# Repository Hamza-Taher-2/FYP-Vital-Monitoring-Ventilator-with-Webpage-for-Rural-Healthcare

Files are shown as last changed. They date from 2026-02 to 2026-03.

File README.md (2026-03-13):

# FYP-Vital-Monitoring-Ventilator-with-Webpage-for-Rural-Healthcare

Smart Portable Vital Monitoring Ventilator

Student: Muhammad Hamza Taher
Supervisor: Dr Munira Raja
Assessor: Dr Roberto Ferrero

A low-cost portable ventilator and vital monitoring system designed for rural healthcare environments with limited access to electricity and medical infrastructure.

The system integrates patient monitoring sensors, a Raspberry Pi Pico W microcontroller, wireless data transmission, and a solar-powered energy system to create a portable and sustainable medical support device.

Project Overview

- Rural areas in South Asia suffer from high levels of chronic respiratory diseases, contributing to approximately 12% of deaths across the region. 

- Poster Update 5

- Combined with limited access to medical facilities, this leads to increased mortality rates.

- This project aims to develop a cost-effective monitoring ventilator system that can assist healthcare workers by:

- Monitoring patient vital signs

- Providing ventilation assistance

- Transmitting medical data through a webpage

- Operating in low-power environments using solar energy

Key Features

- Portable ventilator monitoring system

- Real-time vital sign monitoring

- Wireless data transmission via WiFi

- Fast responsive companion webpage

- Alarm system for abnormal readings

- Solar powered charging system

- Adjustable ventilator operation

- Low-cost hardware design

System Architecture

- The system is built around a Raspberry Pi Pico W, which manages:

- Sensor data acquisition

- Motor control for ventilation

- LCD display updates

- Wireless webpage communication

- The microcontroller balances these tasks to avoid signal starvation and maintain stable operation. 

Hardware Components
- Component	Purpose
- Raspberry Pi Pico W	Main microcontroller
- Vital Sign Sensors	Monitor patient health data
- Servo / Motor System	Controls ventilator airflow
- LCD Display	Displays patient data locally
- LiPo Battery	Portable power source
- Solar Tracker	Tracks sunlight to maximise energy capture
- Solar Panel	Renewable power supply
- ON/OFF Switch	Power control
- Solar Power System

- The system includes a solar tracking module to support operation in areas with limited electricity.

The solar tracker:

- Tracks the sun throughout the day

- Maximises solar panel efficiency

- Converts solar energy into a stable 5V output

- Charges a rechargeable LiPo battery

- This allows the ventilator to operate in off-grid environments. 

Electronics Design

- The circuit was designed using KiCad.

- Key features of the schematic include:

- Shared 3.3V power rail

- I2C communication between sensors and Pico

- Dedicated power subsystem for the LiPo battery

- Direct servo connection for ventilator control

- ON/OFF power control system

- The device boots and initializes sensors before establishing WiFi communication.

Sensor Calibration

- All sensors were calibrated against known reference devices to ensure reliable monitoring.

Temperature

- Reference: Medical thermometer

- Adjustment: Code libraries

- Issues: Sensor refresh rate

Air Pressure

- Reference: Manufacturer datasheet

- Adjustment: Code libraries

- Issues: Tube leakage

Heart Rate

- Reference: Apple Watch

- Adjustment: Library calibration

- Issues: Tube pressure affecting readings

Blood Oxygen (SpO₂)

- Reference: Apple Watch

- Adjustment: Library calibration

- Issues: Adjustments required for darker skin tones

Market Context

- The global medical technology market is expected to reach:

- $712.9 billion by 2030

- IoT monitoring devices represent one of the largest growth sectors, accounting for approximately 18% of the market share. 

- This project demonstrates how low-cost embedded systems can contribute to this growing healthcare technology space.

Future Improvements

- Potential future developments include:

- Improved solar tracker battery system

- Longer wireless transmission range

- Secure global patient database

- Data encryption for medical compliance

- Additional sensors (e.g., ECG monitoring)

- Medical regulatory compliance (WHO standards)

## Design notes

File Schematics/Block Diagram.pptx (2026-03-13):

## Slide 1

Initial Design

Motor

Display - LCD

S1 -
Heart Rate and Blood Oxygen

S2 –
Temperature

MC1 –
Raspberry Pi Pico W

B3 –
Speed

MC2 –
Raspberry Pi Zero 2

Web Page

S3 –
Pressure

KEY
Sensor
Microcontroller
Buttons
Display
Webpage
Motor

B2 –
Volume

B1 –
On/Off

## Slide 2

New Design

B1 –
On/Off

S1 -
Heart Rate and Blood Oxygen

S2 –
Temperature

MC2 –
Raspberry Pi Pico W

MC3 –
Raspberry Pi Pico W

Web Page

S3 –
Pressure

Display - LCD

KEY
Sensor
Microcontroller
Buttons
Display
Webpage
Motor

B2 –
Volume

MC1 –
Raspberry Pi Pico H

Motor

B3 –
Speed

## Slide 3

Old Design

B1 –
On/Off

S1 -
Heart Rate and Blood Oxygen

S2 –
Temperature

MC1 –
Raspberry Pi Pico W

MC2 –
Raspberry Pi Zero 2

Web Page

S3 –
Pressure

Display - LCD

KEY
Sensor
Microcontroller
Buttons
Display
Webpage
Motor

B2 –
Volume

MC1 –
Raspberry Pi Pico H

Motor

B3 –
Speed

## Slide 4

Sem 2 Design

Motor

Speaker

Display - LCD

Heart Rate and Blood Oxygen

Temperature

Raspberry Pi Pico W

Web Page

KEY
Sensor
Microcontroller
Buttons
Display
Webpage
Motor
Speaker

Pressure

B2 –
Volume

B3 –
Speed

B1 –
On/Off

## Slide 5

Temperature

Pressure

Heart Rate

Blood Oxygen

Raspberry Pi Pico W

Newest Design

B1 – On/Off

Display - LCD

B3 – Speed

B2 – Volume

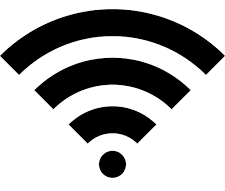
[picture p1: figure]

Speaker

Motor

Web Page

LDR

Pi Pico H

Motor

Button ON/OFF

Battery

Solar Panel

Converter

Output

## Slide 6

LDR

Pi Pico H

Motor

Button ON/OFF

Battery

Solar

Solar Panel

Converter

Output

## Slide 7

Pressure

Heart Rate

Temperature

Pi Pico W

Blood Oxygen

Solar Panel

Button ON/OFF

LDR

B1 – On/Off

Display - LCD

Converter

Pi Pico H

B3 – Speed

B2 – Volume

Speaker

Web Page

Motor

Output

Battery

Motor

NEW NEWEST Design

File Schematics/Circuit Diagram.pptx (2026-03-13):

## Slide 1

Heart D

Heart C

Heart GND

OLD

Pressure V + Temp V + Heart V

Pressure Signal

Pressure GND

Temp GND

Temp signal

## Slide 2

NEW

Heart GND

Pressure V + Temp V + Heart V + Speaker V + LCD V +

Heart D + LCD SDA

Heart C + LCD SCL

Pressure Signal

Speaker GND + Pressure GND

Temp GND

LCD GND

Speaker Signal

Temp signal

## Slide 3

MOTOR

Heart GND

Pressure V + Temp V + Heart V + Speaker V +
LCD V + P1 V + P2 V + Servo V + Humidity V

Heart D + LCD SDA

Heart C + LCD SCL

Servo GND

Pressure Signal

P1 Signal

P2 Signal

Speaker GND + Pressure GND

Temp GND

P1 GND + P2 GND + Humidity GND

LCD GND

Humidity Signal

Speaker Signal

Servo Signal

Temp signal

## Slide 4

FULL

LCD

SCL

SDA

Pressure

Heart

Pot 1

Pot 2

+3V3 Battery

Humid

Servo

Temp

Servo

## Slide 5

Solar Panel

Solar Board

Battery

Switch

SOLAR

LDR

LDR

Resistor

Resistor

Servo

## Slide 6

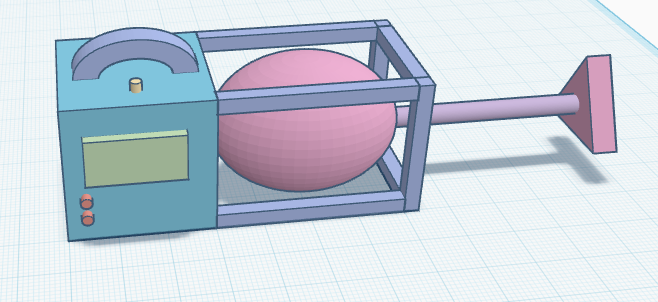
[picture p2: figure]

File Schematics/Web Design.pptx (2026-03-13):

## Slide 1

Dr Akhter’s Monitor Log

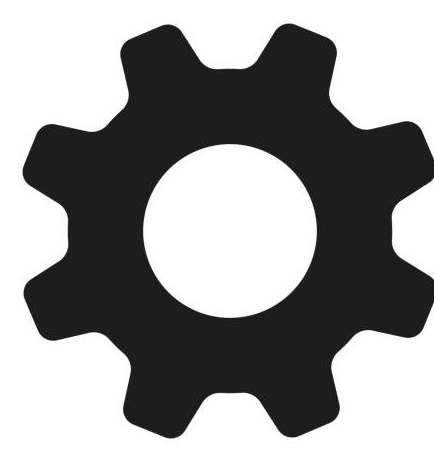
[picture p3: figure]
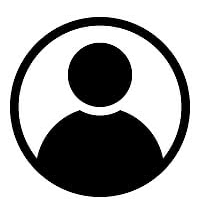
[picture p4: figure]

Patient Information
Patient Name: Simran Khan
Patient ID: 19023
Location: Khulna, Bangladesh
Time: 12:08 BST

Sensor Readings
Heart Rate: 72 BPM
Average Heart Rate: 75 BPM
Peak Heart Rate: 112 BPM
Lowest Heart Rate: 64 BPM
Temperature: 23°C
Blood Oxygen: 98% SpO2
Air Pressure: 80 PaO2
Humidity: 80% HD

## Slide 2

Dr Akhter’s Monitor Log

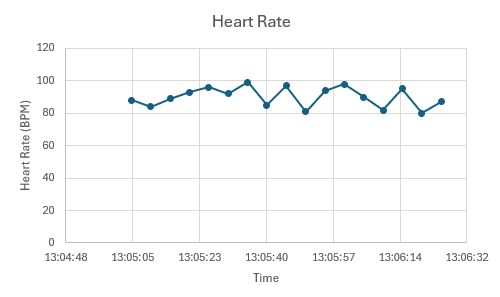
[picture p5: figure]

Patient Information
Patient Name: Simran Khan
Patient ID: 19023
Location: Khulna, Bangladesh
Date: 09/02/2026
Time: 12:08 BST

Sensor Readings
Heart Rate: 72 BPM
Average Heart Rate: 75 BPM
Peak Heart Rate: 112 BPM
Lowest Heart Rate: 64 BPM
Temperature: 23°C
Blood Oxygen: 98% SpO2
Air Pressure: 80 PaO2
Humidity: 80% HD

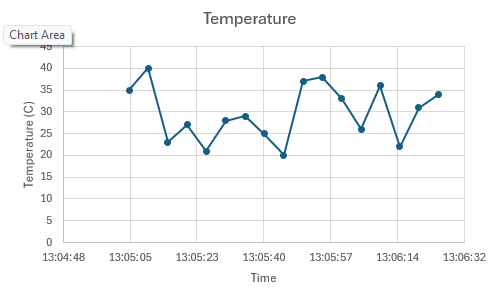
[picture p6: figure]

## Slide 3

Could add diagrams of the heart rate, etc

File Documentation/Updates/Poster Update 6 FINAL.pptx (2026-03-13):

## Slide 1

Smart Portable Vital Monitoring Ventilator with a Companion Webpage for Rural Healthcare

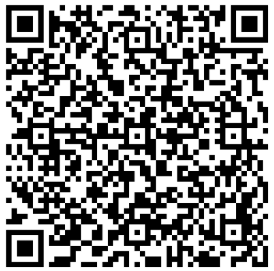
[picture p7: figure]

GitHub

Student: Muhammad Hamza Taher

ID: 201723236

Supervisor: Dr Munira Raja

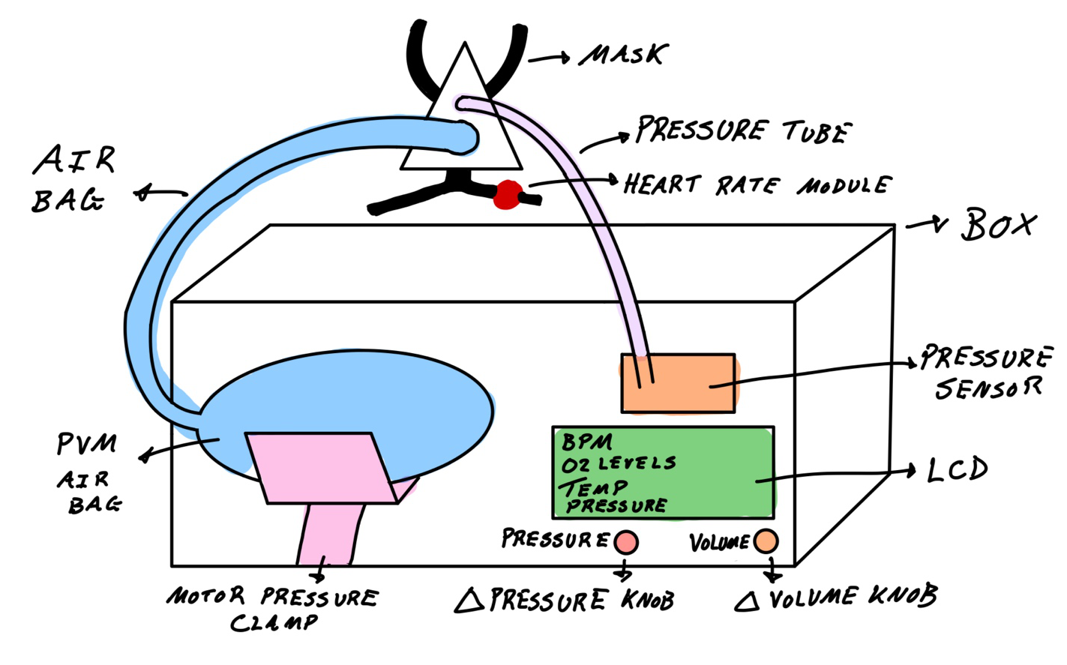
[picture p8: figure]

Fig. 1: Initial Sketch

Assessor: Dr Roberto Ferrero

The design (in Fig. 1) incorporates the following features:
- Pico W to detect patients vitals to display on an LCD and webpage for remote monitoring [2]
- Potentiometer-controlled motor acts as an adjustable ventilator [3]
- Rechargeable battery and alarm system.

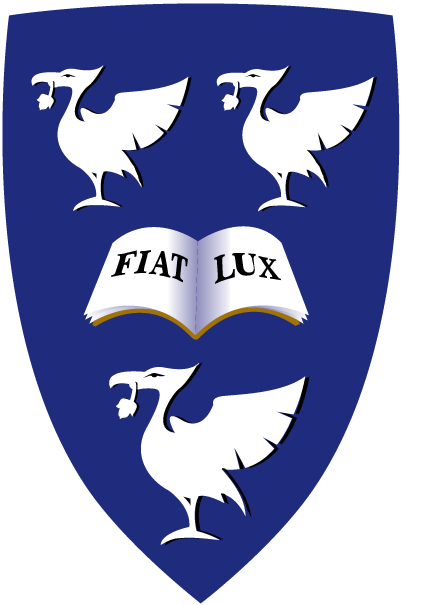
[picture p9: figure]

Introduction

This project aims to develop a system to remotely support health monitoring in rural South Asia via data transmission of vital data to nearby hospitals. [1]
Objectives include:
- Utilising calibrated sensors to measure patient’s vitals
- Display the patient’s vital data on an LCD and Webpage
- Functional ventilator with adjustable setting (speed and pressure)
- Rechargeable battery system for longer duration of use
- Working alarm system activated when thresholds are exceeded

Background Information

The system is a monitoring aid, not a replacement for professional equipment [6].
Future updates includes data encryption and compliance with medical standards (Fig.6)
Design specifications are as follows:
- Heart Rate accuracy: ± 5 BPM
- Web latency: 15ms
- Battery duration: 20 Hours
- Alarm trigger success: 90%

Fig. 6: 3D Mock Up of Design

Specification

The Pico W splits its attention between the motor, LCD, webpage, and sessors to manage signals to stop starvation for a cost-effective design [4].
For areas with low access to power, a solar tracker was designed to track the sun to convert solar energy to a stable 5V output (in Fig.4) [5].

Fig. 4: Block Diagram of Ventilator and Solar Tracker

The KiCAD schematic (in Fig.5) shows a shared 3.3V input and ground with i2C signal pins connecting to a Pico pin. The rechargeable LIPO battery uses a power sub-circuit and direct connection to the servo. Controlled by an ON/OFF button with the device booting until connected to WIFI.

Fig. 5: Ventilator System Schematic

Implementation and Design

Estimated to grow to $712.9 bn by 2030, the medical technology market is a fast-growing industry with IoT monitoring devices at the highest market share of 25%,(in Fig.2) reaching $40.7 bn by 2030 [7]

Fig. 2: Market Data of Medical Data

Rural areas in South Asia have high levels of chronic respiratory diseases resulting in 12% of deaths across all regions [8]. Paired with low medical access results in high mortality rates.

Fig. 3: Air Pollution in South Asia

Market Research

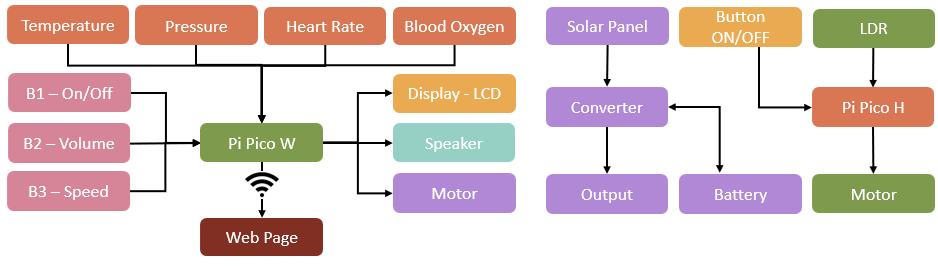
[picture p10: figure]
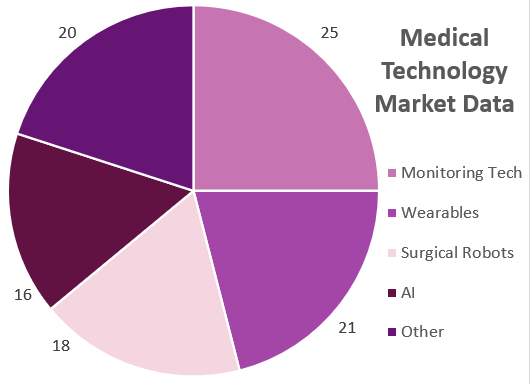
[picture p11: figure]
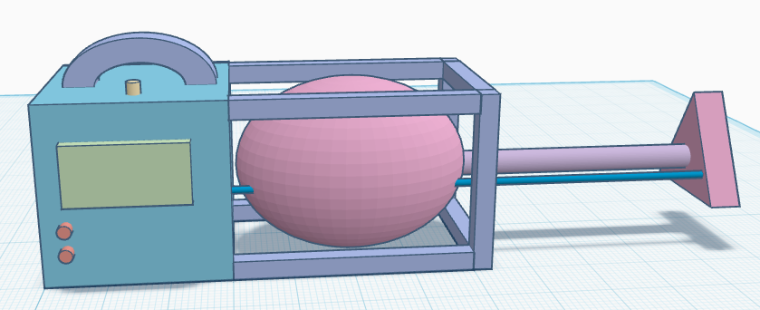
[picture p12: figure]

References

1. Webster, J. (2017). Medical Instrumentation: Application and Design.
2. Analog Devices (2019). MAX30102 Pulse Oximeter and Heart-Rate Sensor Datasheet.
3. Just Do Electronics (2022). DIY Ventilator Using Arduino.
4. Raspberry Pi Foundation (2021). Getting Started with Raspberry Pi Pico.
5. Circuit Digest (2020). Sun Tracking Solar Panel Using Arduino
6. World Health Organization (2019). Technical Specifications for Medical Devices.
7. Nagarro (2024). Medical Devices Market Summary
8. IQAir (2024). Global Air Quality Map

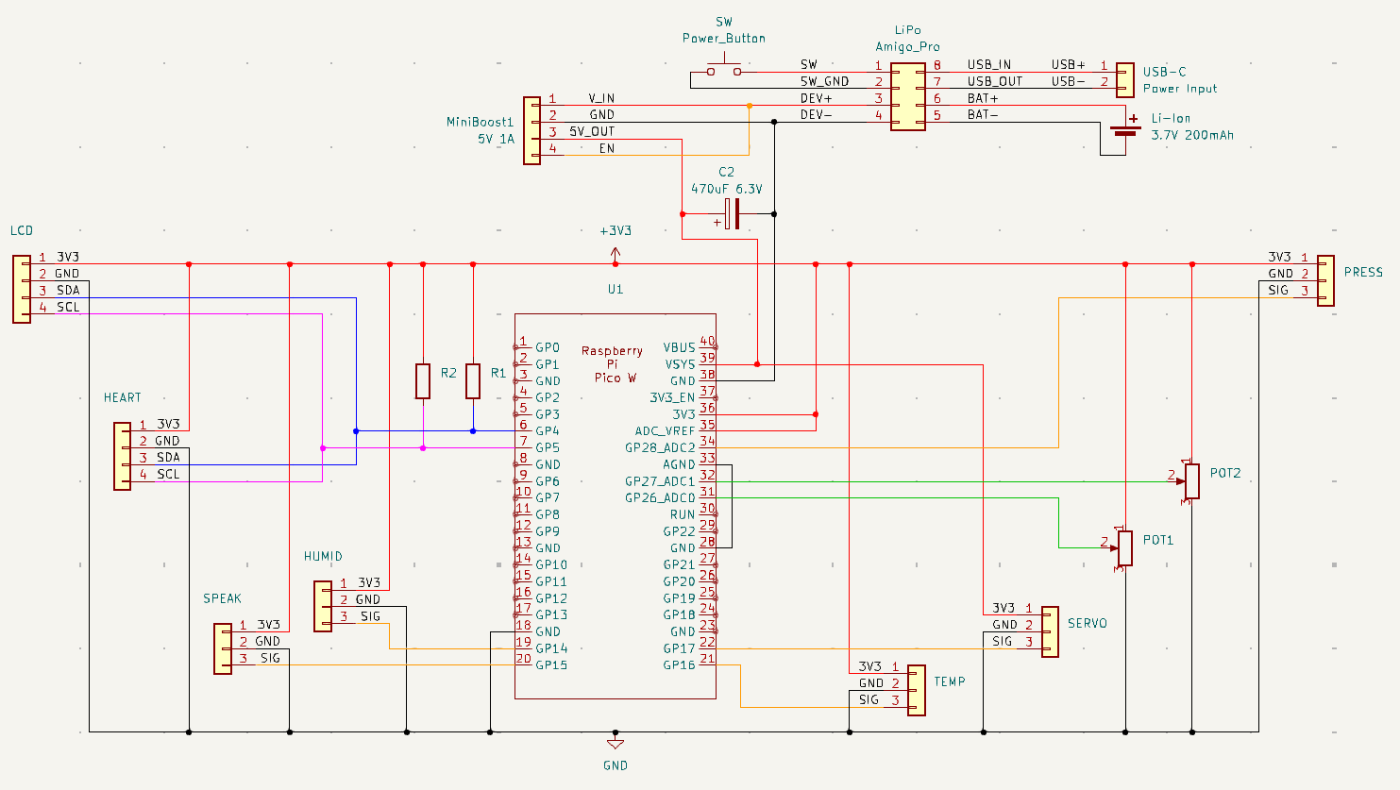
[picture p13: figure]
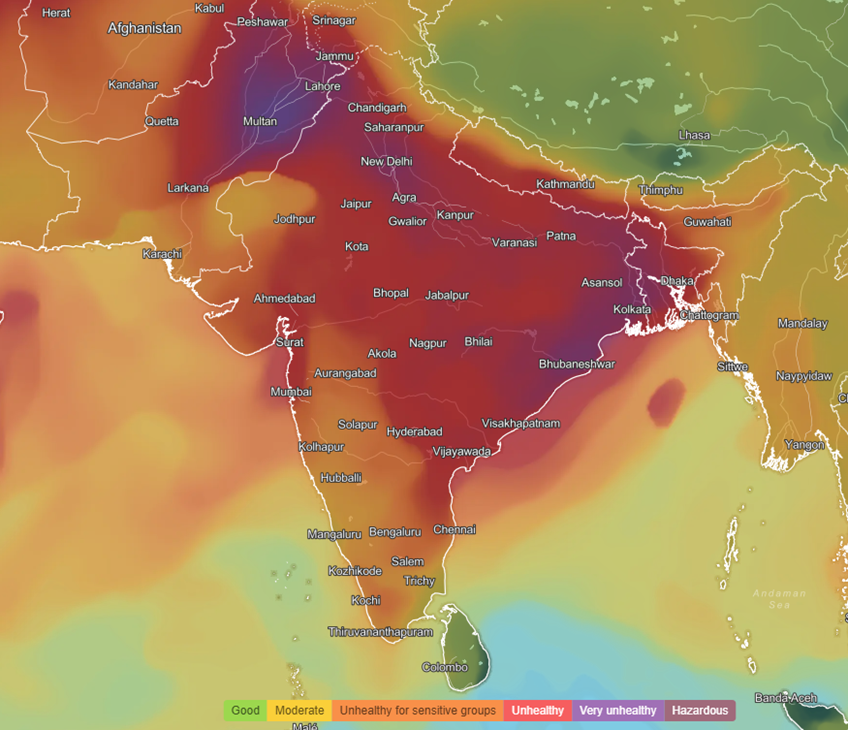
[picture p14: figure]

Sensor Calibration Results and Discussion

Conclusion

Temperature:
Figure 8 shows
Calibrated against:
- Thermometer
Adjusted using:
- Code Libraries
Issues came from:
- refresh rate adjustment

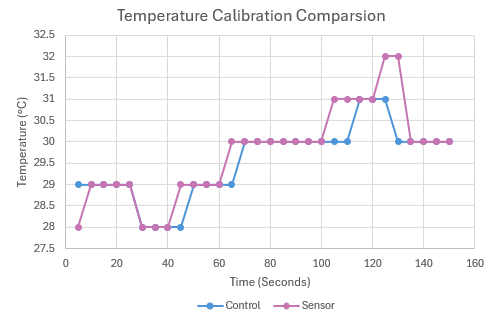
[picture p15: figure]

Fig. 8: Temperature Calibration Graph

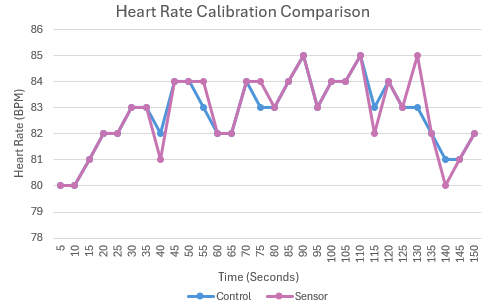
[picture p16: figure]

Fig. 7: Heart Rate Calibration Graph

Heart Rate:
Figure 7 shows
Calibrated against:
- Apple Watch
Adjusted using:
- Code Libraries
Issues came from:
- Adjustments for darker skin

The project was an overall success as the aims were met through the following objectives:
- Responsive data displays
- Calibrated sensors for vital reading
- Adjustable functional ventilator
- Alarm system active when exceeded thresholds
Further improvements include:
- Larger battery capacity for longer time of usage
- Longer transmission range for instant medical data refresh rate
- Global patient database with encryption data
- Added sensors like ECG for better scope of information

Air Pressure:
Figure 9 shows
Calibrated against:
- Medical tool
Adjusted using:
- Code Libraries
Issues came from:
- Tube leakages and diameter

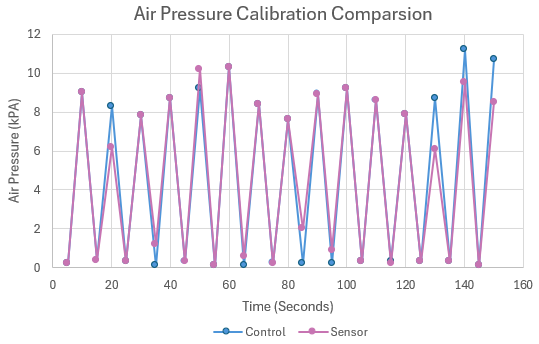
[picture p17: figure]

Fig. 9: Air Pressure Calibration Graph

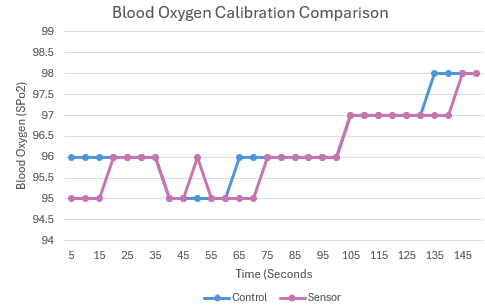
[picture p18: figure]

Fig. 10: Blood Oxygen Calibration Graph

Blood Oxygen:
Figure 10 shows
Calibrated against:
- Apple Watch
Adjusted using:
- Code Libraries
Issues came from:
- Adjustments for darker skin

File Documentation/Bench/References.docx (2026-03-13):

References

Solar tracker

https://circuitdigest.com/microcontroller-projects/building-your-own-sun-tracking-solar-panel-using-arduino

Ventilator

https://justdoelectronics.com/diy-ventilator-using-arduino/

Webpage

https://bytesnbits.co.uk/web-control-panel-web-page/

Heart rate

https://www.analog.com/media/en/technical-documentation/data-sheets/max30102.pdf

Motor

https://components101.com/motors/mg996r-servo-motor-datasheet

Arduino IDE

https://docs.arduino.cc/software/ide-v2/tutorials/getting-started-ide-v2/

Pico

https://pip-assets.raspberrypi.com/categories/610-raspberry-pi-pico/documents/RP-008276-DS-1-getting-started-with-pico.pdf?disposition=inline

Systematic engineering approach

https://www.academia.edu/85557058/Pahl_Beitz_Engineering_Design_A_Systematic_Approach

IoT

https://ieeexplore.ieee.org/document/7123563

Biomedical Sensors

https://studentebookhub.com/wp-content/uploads/2024/preview/9781119457336.pdf

Medical devices guide

https://www.who.int/publications/i/item/WHO-2019-nCoV-MedDev-TS-O2T.V2

Solar tracker

https://circuitdigest.com/microcontroller-projects/building-your-own-sun-tracking-solar-panel-using-arduino

Ventilator

https://justdoelectronics.com/diy-ventilator-using-arduino/

Heart rate

https://www.analog.com/media/en/technical-documentation/data-sheets/max30102.pdf

Pico

https://pip-assets.raspberrypi.com/categories/610-raspberry-pi-pico/documents/RP-008276-DS-1-getting-started-with-pico.pdf?disposition=inline

IoT

https://ieeexplore.ieee.org/document/7123563

Biomedical Sensors

https://studentebookhub.com/wp-content/uploads/2024/preview/9781119457336.pdf

Medical devices guide

https://www.who.int/publications/i/item/WHO-2019-nCoV-MedDev-TS-O2T.V2

Circuit Digest (2020). Sun Tracking Solar Panel Using Arduino.

Just Do Electronics (2022). DIY Ventilator Using Arduino.

Analog Devices (2019). MAX30102 Pulse Oximeter and Heart-Rate Sensor Datasheet.

Raspberry Pi Foundation (2021). Getting Started with Raspberry Pi Pico.

Al-Fuqaha, A. (2015). IEEE Communications Surveys & Tutorials.

Webster, J. (2017). Medical Instrumentation: Application and Design.

World Health Organization (2019). Technical Specifications for Medical Devices.

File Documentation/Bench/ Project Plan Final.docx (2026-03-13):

DEPARTMENT OF ELECTRICAL ENGINEERING & ELECTRONICS

# Project Plan for project ‘Smart Portable Respiratory Assistance and Monitoring Device for Rural Healthcare’

Author: Muhammad Hamza Taher (201723236)

Project Supervisor: Dr Munira Raja

Project Assessor: Dr Roberto Ferrero

Declaration of academic integrity

By submitting this work, I confirm that I have read and understood the University’s Academic Integrity Policy.
By submitting this work, I confirm that I have acted honestly, ethically and professionally in conduct leading to assessment for the programme of study.
By submitting this work, I confirm that the work I am submitting is my own. I have not commissioned production of the work from a third party or used artificial intelligence software in an unacceptable manner to generate the work*. I have not copied material from another person or source, nor committed plagiarism, nor fabricated, falsified or embellished data when completing the attached piece of work. I have not colluded with any other student in the preparation and/ or production of this work.
*Software applications include but are not limited to, ChatGPT, Bing Chat, DALL.E, Bard

List of Tables

1. Project Requirements ………………………………………………………………………………………………6
2. Skills Audit …………………………………………………………………………………………………………..…13
3. Components List ……………………………………………………………………………….……………………14
4. Resource List …………………………………………………………………………….……………………………14

## 1. Project Scope

This project focuses on the development of an affordable biomedical health monitoring device which records and transfers vital data of the patient wearing the device to a secure mobile app used by a doctor in the nearest hospital to diagnose and give advice on how to proceed with either medication or a hospital visit [1]. The market for monitoring devices is rapidly growing, yet to reach its peak, allowing this device to learn from others in the market and improve their design for rural use [2] [3].

South Asia, through the effects of colonisation, exploitation, and political struggles, has caused many areas to lack access to instant healthcare [4]. As there are no solid transportation links between these rural areas to the nearest hospital residents who are ill take longer alternative routes, such as walking or by horseback, which can worsen their condition [5] [6]. The time taken to arrive at the hospital is further affected by the busyness of the hospital and the availability of doctors at that moment in time to see patients without a set appointment [7]. By utilising this device, rural access to healthcare will be transformed as patients will have real-time online health consultation and monitoring, while doctors can have easier access to patients’ vitals to make decisions [8].

The device is portable and durable using its laser cut MDF/PLA body while having a CPAP mask and breathing tube which works with a motorised pump with 3D printed components to act as a ventilator [9] [10]. The mask has built in sensors modules (temperature, heart rate, blood oxygen, and air pressure) to measure the vitals of the patient [11]. A Raspberry Pi Pico receives the sensor data along with button input (to control the ventilator and power) [12]. The data is sent to a Raspberry Pi Zero-2 which displays the information on the LCD/OLED display while sending it wirelessly to the webpage [13].

## 2. Project Objectives

Code -> SX: WY = Semester X: Week Y

Heart Rate and Blood Oxygen:

Program a hardware module on the mask that accurately measures the Heart Rate (in BPM between 0-240BPM) and Blood Oxygen (between 70% to 100% SpO2) of the patient which display the measurements on the website and LCD, while showing real-time changes in the readings (within 5s of real-time). This is a critical feature for the project’s success as it’s a major vital measure, which must be functional by S1W5 and calibrated by S2W2.

Temperature:

Program a hardware module on the mask that accurately measures the temperature (0°C to 100°C) of the patient which display the measurements on the website and LCD, while showing real-time changes in the readings (within 5s of real-time). This is a critical feature for the project’s success as it’s a major vital measure, which must be functional by S1W6 and calibrated by S2W4.

Air Pressure:

Program a hardware module on the mask that accurately measures the respiratory pressure (70mmHg to 100mmHg PaO2) of the patient which display the measurements on the website and LCD, while showing real-time changes in the readings (within 5s of real-time). This is a critical feature for the project’s success as it’s a major vital measure, which must be functional by S1W6 and calibrated by S2W4.

Knobs:

Have functional knobs to control the ventilator, and ON/OFF switch for long term durable use which are tested with speed of change on the ventilator and circuit. Needed to help adjust the ventilator for safety using potentiometer, to be functional by S1W12 and fully tested by S2W6.

Display:

Set a readable LCD/OLED display that can be read clearly from up to 3 meters away to let medical practitioners read the vitals. Needed for accessible medical info for people and be functional by S1W5 and fully tested by S2W3.

Data transmission:

Creating a continuous secure data flow from the microcontroller to the website to display data from sensors which are used for diagnosis, with speed and delay measure using bandwidth and online speed tests for further calibration. An integral part of the project to display rapid continuous real time vital measurements on the website for healthcare practitioners as its needed to be functional by S1W8 and fully tested by S2W7.

Power:

Develop an efficient power system using a 12V lithium-ion battery to power both microcontroller and components with specified voltages using resistors which is tested using a stopwatch, a Multimeter and log calculations for charge and discharge of power with the power supply across the circuit. Necessary to provide the right amount of voltage and current to the circuit for a working device being functional by S1W8 and calibrated by S2W5.

Mask Design:

Design/manipulate a mask so it has room for the sensors to safety is without causing any injury (tested by finding and sanding down sharp edges and adding cushions). Needed for safe use by patients, and to be functional by S1W10 and fully tested by S2W6.

Pump Design:

Create an efficient ventilator pump design which can be adjusted for volume and speed using functional knobs which is measured using an air pressure monitor and balloons to find correct calibration for certain configurations. Necessary for the ventilator to adjust for patient comfortable with it being functional by S1W10 and fully tested by S2W6.

Box Design and Portability:

Designing a professional portable, durable dox design out of PLA/MDF material which can withstand being dropped by 1 metre and having no sharp edges lesser than 45 degrees while having a supportive rack for the ventilator and mask. Necessary to ensure it can survive rough climates and be portable for long distances while being functional by S1W12 and fully tested by S2W7.

## 3. Project Requirements

Category | Identifier | Description
Environmental Measurement | ENV-01 | Humidity Range: Measure environmental humidity between 0% to 100% with a resolution of ± 1%. Tested against a calibrated sensor for accuracy.
Environmental Measurement | ENV-02 | Temperature Range: Measure body temperature between 0°C to 100°C with a resolution of ± 1°C. Tested against a calibrated sensor for accuracy.
Medical Measurement | MED-01 | Heart rate Range: Measure 0-240BPM with a resolution of ±1BPM. Tested against a calibrated sensor for accuracy.
Medical Measurement | MED-02 | Blood Oxygen Range: Measures oxygen saturation between 70% to 100% SpO2 with a ±2% resolution. Tested against a calibrated sensor for accuracy.
Medical Measurement | MED-03 | Blood Oxygen response Time: Gains a stable SpO2 reading within 5 seconds with a ±2% error margin. Tested against a calibrated sensor for accuracy.
Medical Measurement | MED-04 | Air Pressure Range: Measures air pressure between 70mmHg to 100mmHg PaO2 with a ±2% resolution. Tested against a verified calibrated sensor for accuracy.
System Performance | SYS-01 | Sensor Sampling Rate: Internal sensor sampling frequency ≥50Hz for rapid data capture. Verified using stopwatch and calibration.
System Performance | SYS-02 | Sensor to Display Latency: Time delay between sensor detecting new reading to LCD display ensuring its <250ms.
System Performance | SYS-03 | Sensor to Webpage Latency: Time delay between sensor detecting new reading to webpage display ensuring its <500ms.
System Performance | SYS-04 | Display Update Rate: Ensure the LCD refreshes at >25fps for smooth visuals.
Connectivity and Security | SEC-01 | Webpage Reconnection: Automatically reconnect to the website within 5ms of a disconnection, for continuous data communication.
Connectivity and Security | SEC-02 | Security and Privacy: Implement a basic encryption to the data and a password login page for the website.
Display and Usability | DIS-01 | LCD Readability: Ensure screen remains on and is readable from 3 meters away for accessibility of info.
Power | POW-01 | Battery Life: Support continuous usage of >10 hours of use per full charge. Validated by repeated discharge from 100%.
Power | POW-02 | Charge Time: Recharges to full 100% capacity (100%) within 3 hours of charging. Validated using a stopwatch.
Safety and Compliance | SAF-01 | Electrical Safety: Ensure devices compile with university electrical safety standard, inspected by technician and supervisor.
Safety and Compliance | SAF-01 | Alarm Function: Alarm to trigger on the website if readings exceed given limits. Tested by devices to achieve extreme reading.
Time Keeping | CLK-01 | Clock Accuracy: Internal clock maintains synchronised within ±30 seconds to local time.

Table 1: Project Requirements

## 4. Work Packages and Methodology

### 3.1 Methodology

Using an engineering decomposition approach, the project is turned into two 2 designs, one across each semester [14]. This approach breaks each design into the individual sensor, module and software to allow for each to be solved and later combined to be tested as the finished device. It also used the agile development method to allow flexibility and additions in each iteration of the project [15].

By using a Gantt chart, weekly meetings, and a logbook, I can keep track of all progress throughout the project. As shown in the Gantt Chart in Appendix 1, the project is split into creating the Initial Prototype in Semester 1 and subsequently an improved Final Design in semester 2 [16].

Semester 1 is broken into:

- Initial Documents, Order, and Research (Yellow)
- Testing Components (Red)
- Designing the Initial Design (Orange)

Semester 2 is broken into:

- Evaluation and creation of the Final Design (Blue)
- Poster and Bench Inspection (Purple)
- Final Specification (Green)

### 3.2 Work Packages

WORK PACKAGE DESCRIPTION
WP Title: | System Requirement and Research | WP number | 1
Start Event: | Project introduction and Research Phase
Duration: | 3 weeks

Objectives:

Initial research into the system requirements, circuit design, and needed components of the device along with success criteria, methodology and lab schedule to meet deadlines

Task Description:

- Define the functional and non-functional system requirements, aims and objectives
- Create the methodology, lab schedule, and production process

Inputs:

- Project proposal and description
- Research onto existing products and their uses
- Supervisor input on limitation and goals

Interfaces/links with other tasks or WPs:

- Creates foundation for WP2 (Hardware Development) and WP2 (Software Development)
- Its output influences all other work packages which use the success criteria found

Deliverables:

- Methodology and lab schedule
- Assessment Project Plan document

WORK PACKAGE DESCRIPTION
WP Title: | Hardware Development | WP number | 2
Start Event: | Completion of WP1
Duration: | 3 weeks

Objectives:

Select components based on parameters to test individually in the prototype design with microcontroller, battery, and display integration.

Task Description:

- Design and develop the systems hardware components
- Integrate sensors, power systems, and display.

Inputs:

- Requirements and achieved products from WP1
- Sensor data sheets and specification

Interfaces/links with other tasks or WPs:

- Links and closely connected to WP3 (Software Development) for firmware compatibility
- Helps feeds into WP5 (system integration and testing)

Deliverables:

- Assemble hardware for prototype 1
- Circuit schematics and design with correct documentation

WORK PACKAGE DESCRIPTION
WP Title: | Software Development | WP number | 3
Start Event: | Hardware design start of WP2
Duration: | 2 weeks

Objectives:

Develop the firmware to connect components to the microcontrollers to enable communication been components, ready for web connection,

Task Description:

- Write embedded C/C++ code for each of the sensors for data acquisition
- Implement wireless communication for data transmission

Inputs:

- Hardware configurations from WP2
- Development tools and libraries for the microcontroller

Interfaces/links with other tasks or WPs:

- Interfaces with W2 (Hardware Development) for firmware integration
- Provides data communication framework for WP4 and WP5

Deliverables:

- Embedded C/C++ firmware code
- Software testing documentation

WORK PACKAGE DESCRIPTION
WP Title: | Web Development | WP number | 4
Start Event: | Completion of WP3
Duration: | 2 weeks

Objectives:

Design the companion website to display the health data from the sensors and connect it to the microcontroller.

Task Description:

- Creates an application to receive and display transmitted data
- Development of a user-friendly interface

Inputs:

- Data transmission firmware from WP3
- UX design guidelines for a clean easy to use interface

Interfaces/links with other tasks or WPs:

- Works alongside WP3 for data communication
- Connects to WP5 and WP6 for system testing and validation

Deliverables:

- Functional web prototype that communicates with the device

WORK PACKAGE DESCRIPTION
WP Title: | System Integration and Testing | WP number | 5
Start Event: | Completion of WP2, WP3, and WP4
Duration: | 2 weeks

Objectives:

Integrate all previous subsystems into an operational prototype (able to sense health data and display on LCD and website) to test and identify weaknesses and ways to optimise the design.

Task Description:

- Integrate all the sub-systems (hardware, software, and firmware) to one model
- Evaluate the compete initial porotype’s system performance and stability

Inputs:

- Working prototypes from previous Work Packages
- Test equipment and software tools

Interfaces/links with other tasks or WPs:

- Directly dependant of WP2, WP3, and WP4
- Creates the foundation for WP6 (testing and validation

Deliverables:

- Integrated evaluation and improvement report
- Create the hardware-software interface documentation

WORK PACKAGE DESCRIPTION
WP Title: | Testing and Validation | WP number | 6
Start Event: | The completion of the initial prototype, WP5
Duration: | 3 weeks

Objectives:

Compare prototype readings to accurate references to calibrate sensors and optimising overall device design such as website, circuit schematics, etc.

Task Description:

- Validate and test the systems accuracy, safety and reliability
- Verify and understand the correct data transmission and alarm

Inputs:

- Integrated systems from WP5
- Calibration instruments and reference data

Interfaces/links with other tasks or WPs:

- System systems from WP5 for validation
- Prepares changes for WP5 in creating the final design

Deliverables:

- Validation and calibration reports
- Transmission and data accuracy for changes
- Optimisation of circuit diagram for the final design

WORK PACKAGE DESCRIPTION
WP Title: | Creation of the Final Design | WP number | 7
Start Event: | The completion of testing and validation of the initial prototype, WP6
Duration: | 4 weeks

Objectives:

Creating the final design with optimised data from the WP6 to have an efficient device that can accurately display health data.

Task Description:

- Find ways to optimise the initial protype for the final design
- Creating the final design using optimised circuit design

Inputs:

- Test data from WP5
- Validation reports from WP6 for calibration and repair

Interfaces/links with other tasks or WPs:

- Links with WP2, WP3, and WP4 for all the created design
- Needed for the final documentation and report of the project

Deliverables:

- The final design which has been optimised for bench inspection
- Validated and correct test data
- Information for the final documentation

WORK PACKAGE DESCRIPTION
WP Title: | Documentation | WP number | 8
Start Event: | Completion of the final design
Duration: | 3 weeks

Objectives:

The collection of all circuit diagram, code and test results to produce the final specification, information for bench inspection, and academic poster.

Task Description:

- Combination and collection of all research, test results, diagram and code of the project
- Creation of the final specification report, bench inspection presentation, and poster

Inputs:

- Output of all the previous work packages
- Project logs and validation reports

Interfaces/links with other tasks or WPs:

- Combines all previous work packages (WP1-7)
- Provides the final material for submission and marking

Deliverables:

- Collection of all project documents
- Final report, presentation, and academic poster

## 5. Skills and Resource Audit

### 4.1 Skills Audit

Skills | Level | Training Needs
Circuit design with soldering and PCB development | Proficient | - Learn to create and design PCBs for commercial use - Improving current soldering skills - Watch YouTube videos on how to efficiently design circuits
Embedded systems Programming (C for Raspberry Pi) | Proficient | - Practice with real time labs - YouTube videos and tutorials on using raspberry pi - Coding websites on C and C++
Sensor integration design | Proficient | - Check specification of sensors for compatibility - Recap experience from last 2 projects which used sensors
Battery and power system design | Intermediate | - YouTube videos and tutorials on using rechargeable batteries - Practice in labs - Voltage divider calculations
Calibration and accuracy testing | Proficient | - Practice in labs using sensors - Comparing accuracy of sensors to real-life device
Experiment design | Proficient | - Understand objectives and aims of the experiment - Try different types of testing methods
Analysis of biomedical data | Intermediate | - Research medical data levels and their meanings - Websites for data analysis
Data security and privacy | Intermediate | - Read university guidelines - Utilising teams for data protection
Project management and Documentation | Proficient | - Regular meetings with my supervisor - Track progress via a Gantt chart and milestones
Literature review and scientific research | Proficient | - Research into biomedical testing - Practice writing literature review and improving via feedback
CAD design | Proficient | - Practice creating intricate designs on CAD software - Watch tutorials on YouTube
Website development | Proficient | - Practice creating intricate designs on web dev sites - Watch tutorials on YouTube to find out ways to create a website

Table 2: Skills Audit

### 4.2 Resource Audit

Components List:

Components | Component Type | Why
Raspberry Pi’s | Microcontroller | Dataflow from sensor to website
Heart Rate & Blood Oxygen Module | Module | Measure heart rate and blood oxygen
Temperature Module | Module | Measure temperature
Air Pressure Module | Module | Measure air pressure
Motor | Active | Ventilator pump
Lithium Battery | Active | Battery system
LCD or OLED | Active | Main device display
Potentiometer | Passive | Circuit design and pump adjustments
CPAP Mask and Tube | Support | Ventilator
Safety glasses | Support | General lab safety
Storage box | Support | Component and device storage
Inductors | Passive | Circuit design
Capacitors | Passive | Circuit design
Resistors | Passive | Circuit design
Power bank | Support | Battery system
PLA components (3D printed) | Support | Motor pump
Air pump | Support | Motor pump
Acrylic and wood panels | Support | Motor pump and the box design

Table 3: Components Table

Resources List:

Hardware Resources | Availability | Alternatives
Laser Cutter | EEE lab and Makerspace | Hand cutting materials
3D printer | EEE lab and Makerspace | Laser Cutter
Vinyl Machine | Makerspace | Printing and Drawing
Hand tools | EEE lab | None
Soldering Iron | EEE lab | None
Multimeter | EEE lab | None
Power Supply | EEE lab | None
Oscilloscope | EEE lab | None
Crocodile clips and wires | EEE lab | None
PCB machine | EEE lab | Soldering Components
Devices (MacBook & iPad) | On my person | University Desktops
Autodesk | Online | Other 3D modelling software
VS Code | Online | Other Software IDE
Multisim | Online | Other circuit designer
Web Development site | Online | Other web development site
MATLAB | Online | Other Software IDE
Microsoft Office Package | Online | Google Package

Table 4: Resource Table

## Appendix 1. A Gantt chart

Semester 1:

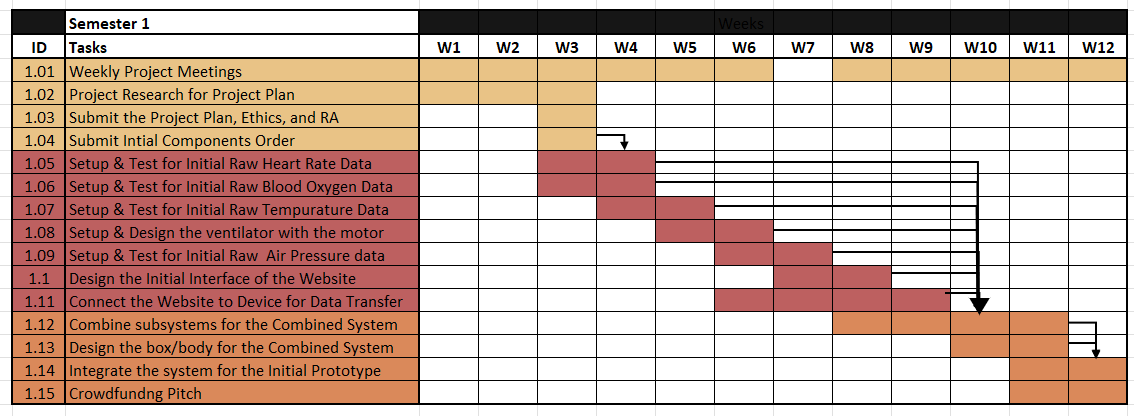
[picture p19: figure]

Semester 2:

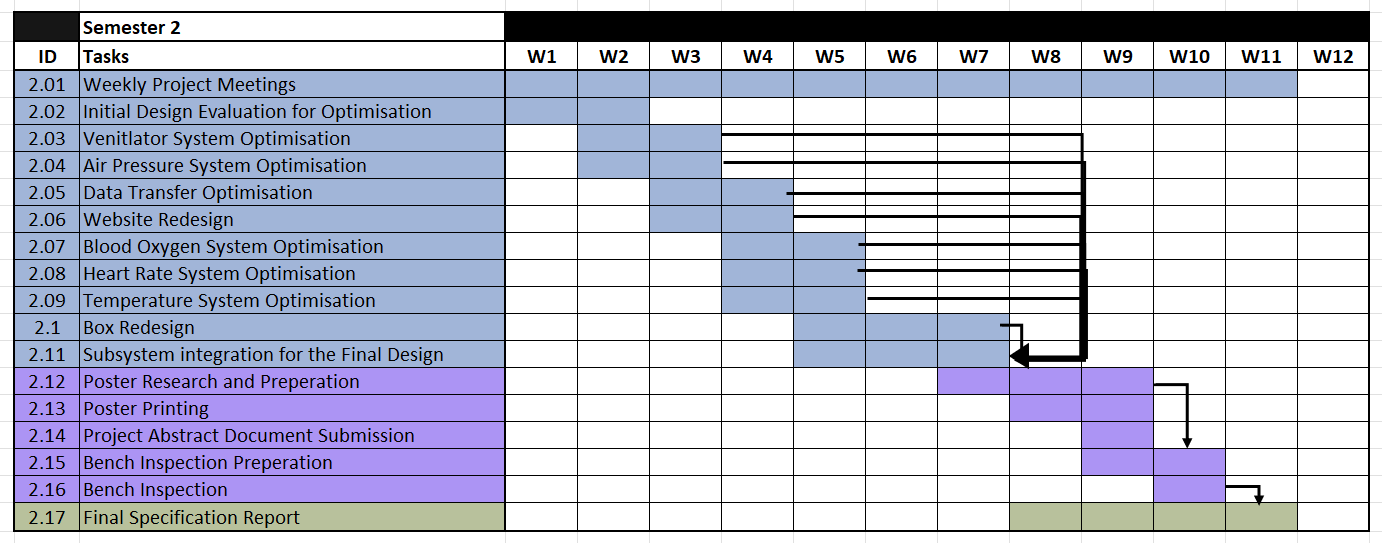
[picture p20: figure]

Whole Year:

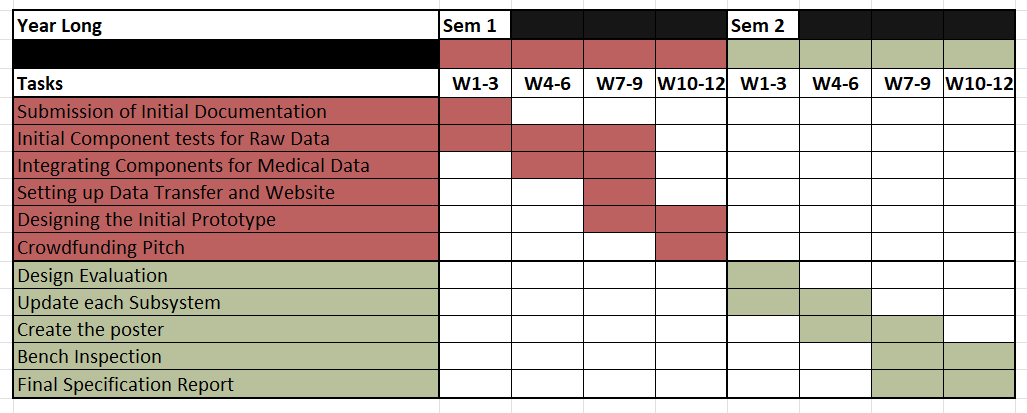
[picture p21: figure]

## Appendix 2. The Risk Assessment Form

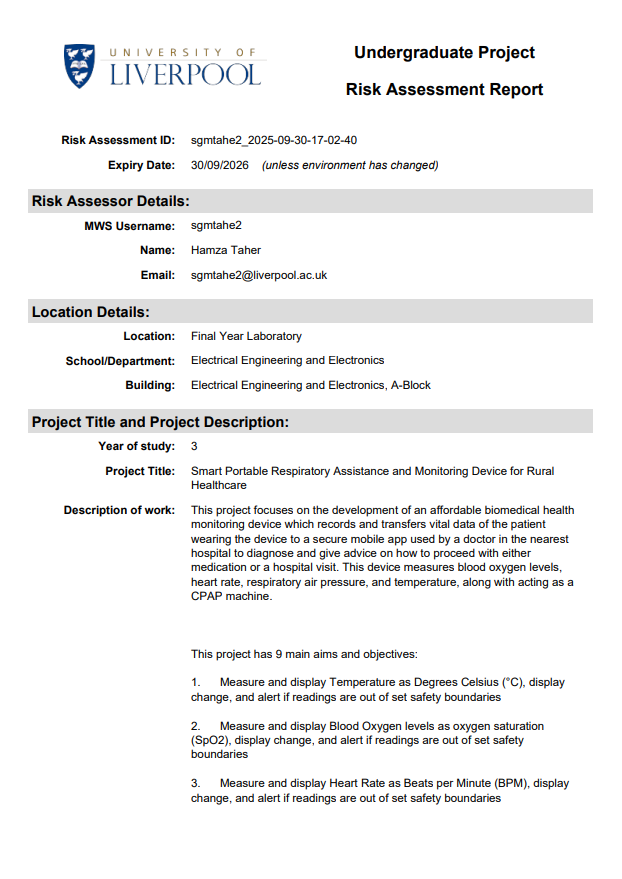
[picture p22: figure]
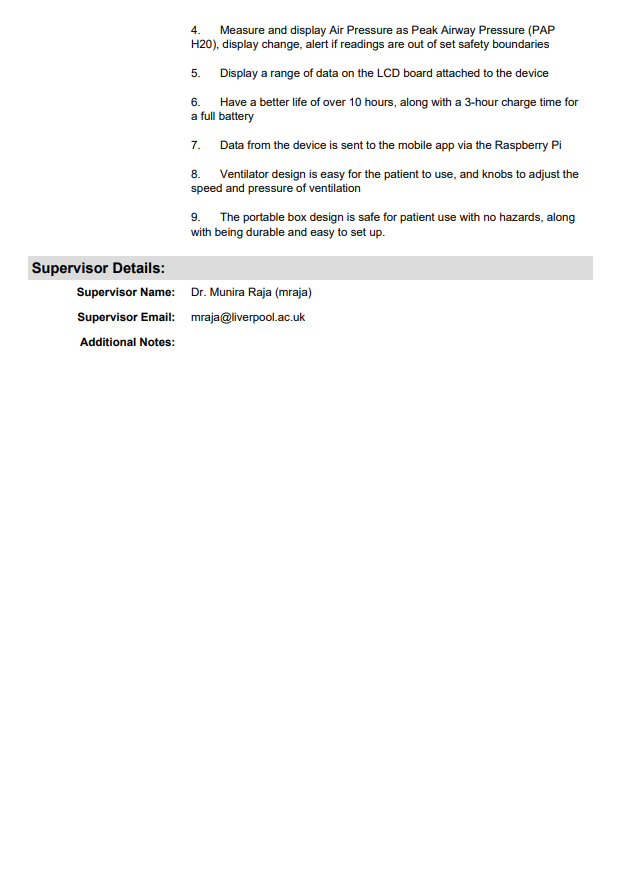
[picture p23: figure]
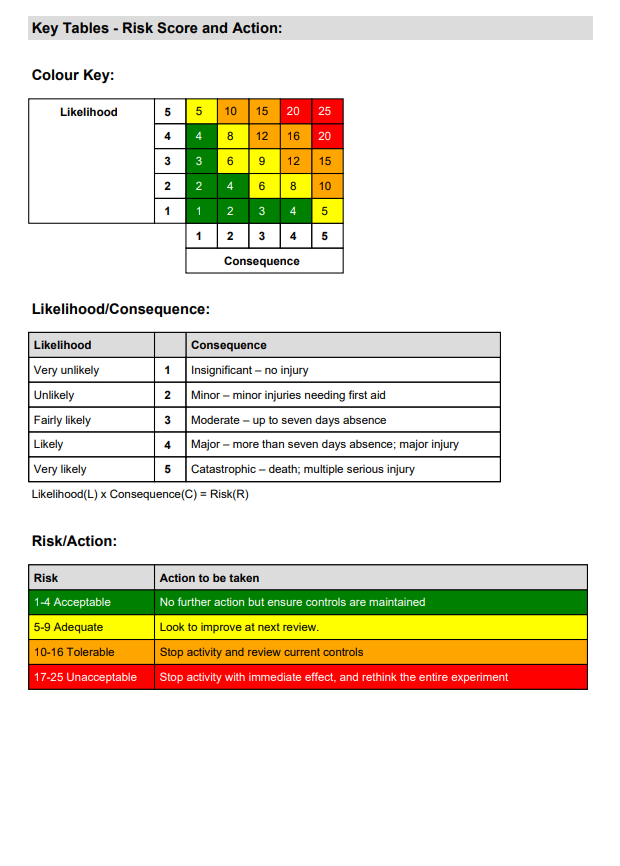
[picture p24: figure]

## Appendix 3. FYP Ethics Self-Assessment.


## Appendix 4. Block Diagram

As seem below, the two central components of the device are the microcontrollers (colour coded green) which are both raspberry pi for compatibility, these are MC1, a Pi Pico, and MC2 which is a Pi Zero 2.

MC1 gets its inputs from the buttons (pink), B1 and B2 control the motor speed for the ventilator while B3 is the on and off switch. MC1 controls the motor (purple) using the changes in input from the buttons. It also controls and takes data from the 3 sensors (orange), S1, S2, and S3 which measure the Heart Rate and Blood Oxygen, Temperature, and Air Pressure. Finally, its connected MC2 where it communicates all the data.

This was designed so MC1 deals with the main bulk of the processing of data and changing inputs to motor movements, so it can send the data to display to MC2 which is connected to the LCD/OLED display (yellow), and wireless transmits the data to the webpage (maroon).


## Appendix 5. Initial Web Design

The webpage has a simple design which shows the doctors name, settings and account details tab in the header.

The data is then split into two boxes; the first box is the patient’s information which includes:

- Name
- ID
- Location
- Time

The bottom box holds the sensor reading which includes:

- Heart Rate
- Average Heart Rate
- Peak Heart Rate
- Lowest Heart Rate
- Temperature
- Blood Oxygen
- Air Pressure
- Humidity


## Appendix 6. References

1. R. Bloss, “Wearable sensors bring new benefits to continuous medical monitoring, real time physical activity assessment, baby monitoring and industrial applications,” Sensor Review, vol. 35, no. 2, pp. 141–145, Mar. 2015, doi: https://doi.org/10.1108/sr-10-2014-722.
2. K. Mahalakshmi, V. R. Palanivelu, and Dharmalingam Kirubakaran, “Global Market Trends in Biomedical Sensors: Materials, Device Engineering, and Healthcare Applications,” Deleted Journal, May 2025, doi: https://doi.org/10.1007/s44174-025-00362-w.
3. N. Kasoju et al., “Digital health: trends, opportunities and challenges in medical devices, pharma and bio-technology,” CSIT, vol. 11, no. 1, pp. 11–30, Apr. 2023, doi: https://doi.org/10.1007/s40012-023-00380-3.
4. “Research Portal,” Miami.edu, 2025. https://scholarship.miami.edu/esploro/outputs/991032631931202976 (accessed Oct. 06, 2025).
5. “Lifelines to rural India: The evolving role of emergency medical services - Healthcare Radius,” Healthcare Radius, Jan. 23, 2025. https://www.healthcareradius.in/features/education/lifelines-to-rural-india-the-evolving-role-of-emergency-medical-services
6. J. Player, “Healthcare Access in Rural Communities in India,” Ballard Brief, 2019. https://ballardbrief.byu.edu/issue-briefs/healthcare-access-in-rural-communities-in-india
7. “India Covid: Hospitals overwhelmed as deaths pass 200,000,” BBC News, Apr. 29, 2021. Available: https://www.bbc.co.uk/news/world-asia-56919924
8. H. S. Kang and M. Exworthy, “Wearing the Future—Wearables to Empower Users to Take Greater Responsibility for Their Health and Care: Scoping Review,” JMIR mHealth and uHealth, vol. 10, no. 7, Jul. 2022, doi: https://doi.org/10.2196/35684.
9. “Library Guides: KnowHow Digital: Makerspace,” Liverpool.ac.uk, 2025. https://libguides.liverpool.ac.uk/knowhow_digital/makerspace (accessed Oct. 06, 2025).
10. “Building opening times | Department of Electrical Engineering and Electronics | University of Liverpool,” Liverpool.ac.uk, 2025. https://www.liverpool.ac.uk/electrical-engineering-and-electronics/about/opening-times/ (accessed Oct. 06, 2025).
11. van Noort, F. L. Becking-Verhaar, Wilmieke Bahlman-van Ooijen, M. Pel, Harry van Goor, and Getty Huisman-de Waal, “Three Years of Continuous Vital Signs Monitoring on the General Surgical Ward: Is It Sustainable? A Qualitative Study,” Journal of Clinical Medicine, vol. 13, no. 2, pp. 439–439, Jan. 2024, doi: https://doi.org/10.3390/jcm13020439.
12. “Raspberry Pi Pico,” The Pi Hut, 2022. https://thepihut.com/products/raspberry-pi-pico?srsltid=AfmBOopZAoOXyodEYWeIjK_Ip-93sJLPWxYtOGIPfFAhp0T3pGiUPEAR (accessed Oct. 06, 2025).
13. “Raspberry Pi Zero 2,” The Pi Hut. https://thepihut.com/products/raspberry-pi-zero-2
14. Nima Bonyadi, Riccardo Talami, and B. Lee, “Breaking-down Building Design Problems with Decomposition Approaches: A Review,” Energy and Built Environment, May 2025, doi: https://doi.org/10.1016/j.enbenv.2025.05.005.
15. A. Omonije, “Agile Methodology: A Comprehensive Impact on Modern Business Operations,” ResearchGate, Feb. 06, 2024. https://www.researchgate.net/publication/377979833_Agile_Methodology_A_Comprehensive_Impact_on_Modern_Business_Operations
16. J. Geraldi, “Gantt Charts revisited: a Critical Analysis of Its Roots and Implications to the Management of Projects Today,” ResearchGate, 2012. https://www.researchgate.net/publication/263571905_Gantt_charts_revisited_A_critical_analysis_of_its_roots_and_implications_to_the_management_of_projects_today

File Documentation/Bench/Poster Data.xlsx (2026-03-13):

 |  |  |  |  | Pot Angle | Oscilation Time | Pot Angle | Oscilation Angle
Type | Size |  |  |  | (Pot %) | Full Osc (Sec) | (Pot %) | (Pot Degree)
Monitoring Tech | 25 |  |  |  | 100% | 0.6 | 100% | 90
Wearables | 21 |  |  |  | 75% | 1.3 | 75% | 80
Surgical Robots | 18 |  |  |  | 50% | 2.7 | 50% | 50
AI | 16 |  |  |  | 25% | 3.9 | 25% | 30
Other | 20 |  |  |  | 0% | 0 | 0% | 0
 | 100
 |  | time | Control | Sensor
 |  | 5 | 80 | 80
 |  | 10 | 80 | 80
 |  | 15 | 81 | 81
 |  | 20 | 82 | 82
 |  | 25 | 82 | 82
 |  | 30 | 83 | 83 |  |  |  |  | Test Number | Result | Test Number | Result
 |  | 35 | 83 | 83 |  |  |  |  | 1 | Pass | 11 | Pass
 |  | 40 | 82 | 81 |  |  |  |  | 2 | Pass | 12 | Pass
 |  | 45 | 84 | 84 |  |  |  |  | 3 | Pass | 13 | Pass
 |  | 50 | 84 | 84 |  |  |  |  | 4 | Pass | 14 | Pass
 |  | 55 | 83 | 84 |  |  |  |  | 5 | Pass | 15 | Pass
 |  | 60 | 82 | 82 |  |  |  |  | 6 | Pass | 16 | Pass
 |  | 65 | 82 | 82 |  |  |  |  | 7 | Fail | 17 | Pass
 |  | 70 | 84 | 84 |  |  |  |  | 8 | Pass | 18 | Pass
 |  | 75 | 83 | 84 |  |  |  |  | 9 | Pass | 19 | Fail
 |  | 80 | 83 | 83 |  |  |  |  | 10 | Pass | 20 | Pass
 |  | 85 | 84 | 84
 |  | 90 | 85 | 85
 |  | 95 | 83 | 83
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

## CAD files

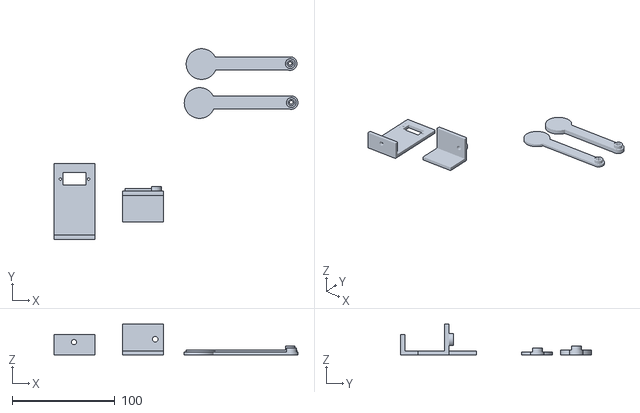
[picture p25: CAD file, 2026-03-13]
CAD_3D/Solar Stand.stl
238.0 x 186.0 x 30.0

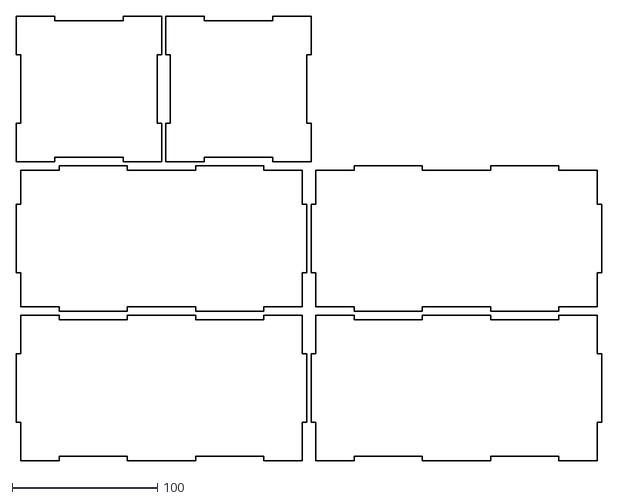
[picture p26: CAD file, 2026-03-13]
CAD_LaserCut/SOLAR BOX.dxf
403.0 x 306.0

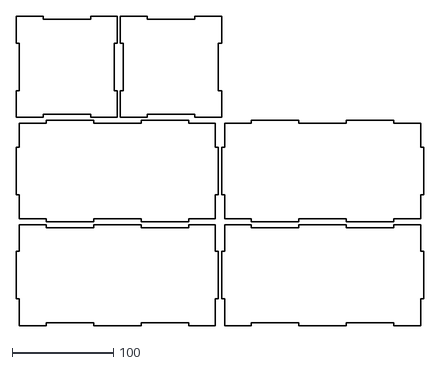
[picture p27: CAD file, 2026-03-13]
SOLAR BOX.dxf
403.0 x 306.0

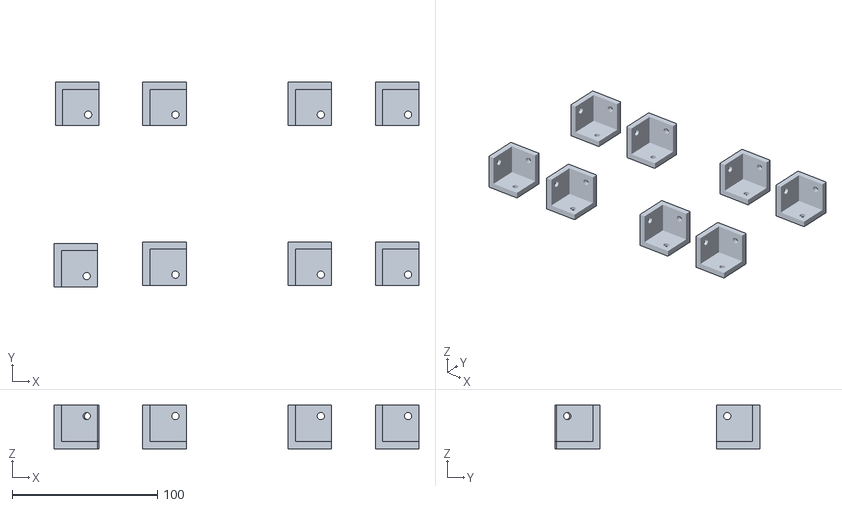
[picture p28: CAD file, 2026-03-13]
CAD_3D/Corner Brackets.stl
251.0 x 141.0 x 30.0

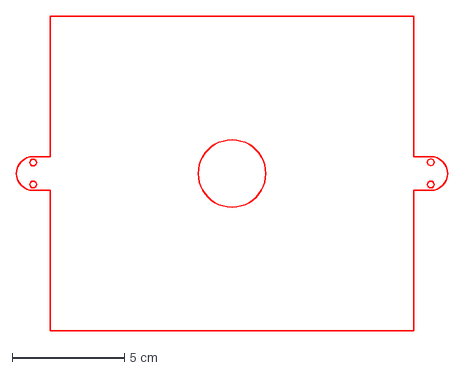
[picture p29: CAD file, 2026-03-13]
CAD_LaserCut/solar plate.dxf
19.2 x 14.0 cm

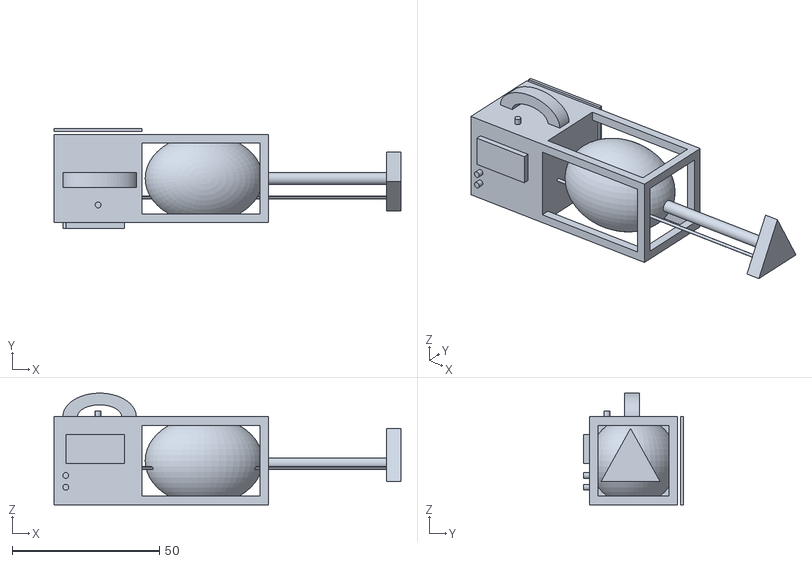
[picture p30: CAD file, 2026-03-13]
CAD_3D/3D Mock Up.stl
118.0 x 34.0 x 38.0

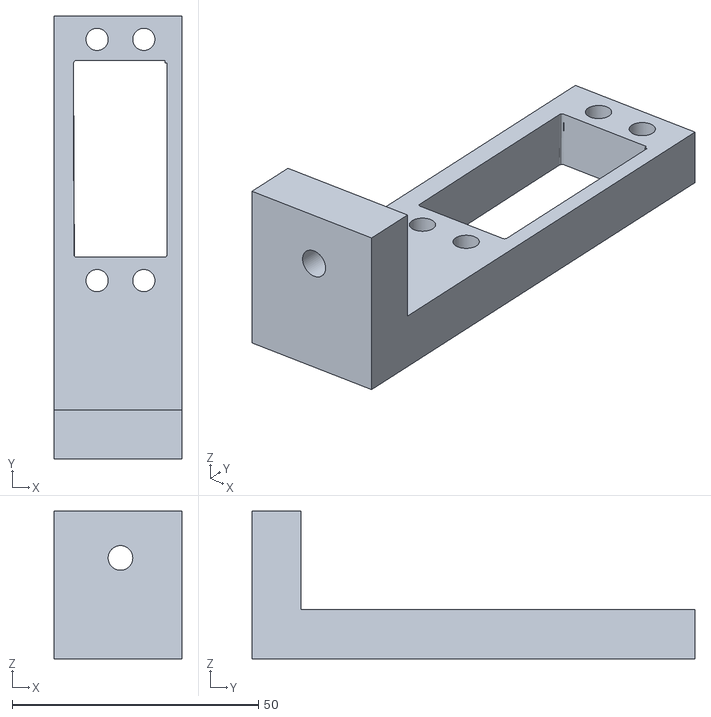
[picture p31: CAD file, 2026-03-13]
CAD_3D/Vent Stand.stl
26.0 x 90.0 x 30.0

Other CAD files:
CAD_3D/Vent Arm.stl

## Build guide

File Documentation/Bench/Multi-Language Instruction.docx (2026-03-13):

Smart Portable Vital Monitoring Ventilator Multi-Language Instruction Kit

## English

How to operate the smart portable vital monitoring respirator

How it works:

- There are built in sensors to detect Blood Oxygen, Heart Rate, Temperature, and Respiratory Pressure in the mask which take and process your current vital data
- The data can be viewed on the small screen while also being sent to a website where a medical professional can monitor your vitals and give a diagnosis or treatment.
- The ventilator has two knows which allow for adjustments of volume and the speed of the respirator to allow comfortable breathing.

Steps:

1. Unbox the device from its packaging carefully
2. Put the mask over your face so all sensors are contacting your skin
3. Put the device on using the green button
4. Wait a minute and then check the LCD to ensure the health data is being taken
5. Adjust the ventilator setting using the knobs for ideal comfort.

Bengali

স্মার্ট পোর্টেবল ভাইটাল মনিটরিং রেসপিরেটর কীভাবে পরিচালনা করবেন

এটি কীভাবে কাজ করে:

- মাস্কে রক্তের অক্সিজেন, হৃদস্পন্দন, তাপমাত্রা এবং শ্বাসযন্ত্রের চাপ সনাক্ত করার জন্য অন্তর্নির্মিত সেন্সর রয়েছে যা আপনার বর্তমান গুরুত্বপূর্ণ তথ্য গ্রহণ করে এবং প্রক্রিয়া করে।

- তথ্যটি ছোট স্ক্রিনে দেখা যাবে এবং একই সাথে একটি ওয়েবসাইটে পাঠানো হবে যেখানে একজন চিকিৎসা পেশাদার আপনার গুরুত্বপূর্ণ তথ্য পর্যবেক্ষণ করতে পারবেন এবং রোগ নির্ণয় বা চিকিৎসা দিতে পারবেন।

- ভেন্টিলেটরের দুটি নো আছে যা আরামদায়ক শ্বাস-প্রশ্বাসের জন্য শ্বাসযন্ত্রের ভলিউম এবং গতির সমন্বয় করতে দেয়।

ধাপ:

১. প্যাকেজিং থেকে সাবধানে ডিভাইসটি খুলে ফেলুন

২. মাস্কটি আপনার মুখের উপর রাখুন যাতে সমস্ত সেন্সর আপনার ত্বকের সাথে যোগাযোগ করে।

৩. সবুজ বোতাম ব্যবহার করে ডিভাইসটি চালু করুন

৪. এক মিনিট অপেক্ষা করুন এবং তারপর স্বাস্থ্য তথ্য গ্রহণ করা হচ্ছে কিনা তা নিশ্চিত করতে LCD পরীক্ষা করুন।

৫. আদর্শ আরামের জন্য নব ব্যবহার করে ভেন্টিলেটর সেটিং সামঞ্জস্য করুন।

Nepali

स्मार्ट पोर्टेबल महत्वपूर्ण निगरानी श्वसन यन्त्र कसरी सञ्चालन गर्ने

यसले कसरी काम गर्छ:

- मास्कमा रगतको अक्सिजन, मुटुको धड्कन, तापक्रम र श्वासप्रश्वासको चाप पत्ता लगाउन निर्मित सेन्सरहरू छन् जसले तपाईंको हालको महत्त्वपूर्ण डेटा लिन्छ र प्रशोधन गर्छ।

- डेटा सानो स्क्रिनमा हेर्न सकिन्छ र वेबसाइटमा पनि पठाइन्छ जहाँ एक चिकित्सा पेशेवरले तपाईंको महत्त्वपूर्ण डेटा निगरानी गर्न र निदान वा उपचार दिन सक्छ।

- भेन्टिलेटरमा दुईवटा यन्त्रहरू छन् जसले आरामदायी सास फेर्न अनुमति दिन भोल्युम र श्वासप्रश्वास यन्त्रको गति समायोजन गर्न अनुमति दिन्छ।

चरणहरू:

१. उपकरणलाई यसको प्याकेजिङबाट सावधानीपूर्वक अनबक्स गर्नुहोस्

२. सबै सेन्सरहरूले तपाईंको छालालाई सम्पर्क गरिरहेका छन् भनेर आफ्नो अनुहारमा मास्क राख्नुहोस्

३. हरियो बटन प्रयोग गरेर उपकरण खोल्नुहोस्

४. एक मिनेट पर्खनुहोस् र त्यसपछि स्वास्थ्य डेटा लिइँदैछ भनी सुनिश्चित गर्न LCD जाँच गर्नुहोस्

५. आदर्श आरामको लागि नबहरू प्रयोग गरेर भेन्टिलेटर सेटिङ समायोजन गर्नुहोस्।

Urdu

سمارٹ پورٹیبل وائٹل مانیٹرنگ ریسپریٹر کو کیسے چلائیں۔

یہ کیسے کام کرتا ہے:

- ماسک میں خون کی آکسیجن، دل کی دھڑکن، درجہ حرارت، اور سانس کے دباؤ کا پتہ لگانے کے لیے سینسر بنائے گئے ہیں جو آپ کے موجودہ اہم ڈیٹا کو لیتے اور اس پر کارروائی کرتے ہیں۔

- ڈیٹا کو چھوٹی اسکرین پر دیکھا جا سکتا ہے جبکہ اسے ایک ویب سائٹ پر بھی بھیجا جا سکتا ہے جہاں ایک طبی پیشہ ور آپ کے وائٹلز کی نگرانی کر سکتا ہے اور تشخیص یا علاج دے سکتا ہے۔

- وینٹی لیٹر کے پاس دو جانیں ہیں جو آرام دہ اور پرسکون سانس لینے کی اجازت دینے کے لئے حجم اور سانس کی رفتار کو ایڈجسٹ کرنے کی اجازت دیتی ہیں۔

مراحل:

1. آلہ کو اس کی پیکیجنگ سے احتیاط سے ان باکس کریں۔

2. اپنے چہرے پر ماسک لگائیں تاکہ تمام سینسر آپ کی جلد سے رابطہ کر سکیں

3۔ آلے کو سبز بٹن کا استعمال کرتے ہوئے لگائیں۔

4. ایک منٹ انتظار کریں اور پھر LCD چیک کریں تاکہ یہ یقینی بنایا جا سکے کہ صحت کا ڈیٹا لیا جا رہا ہے۔

5. مثالی آرام کے لیے نوبس کا استعمال کرتے ہوئے وینٹی لیٹر کی ترتیب کو ایڈجسٹ کریں۔

Punjabi

ਸਮਾਰਟ ਪੋਰਟੇਬਲ ਵਾਈਟਲ ਮਾਨੀਟਰਿੰਗ ਰੈਸਪੀਰੇਟਰ ਨੂੰ ਕਿਵੇਂ ਚਲਾਉਣਾ ਹੈ

ਇਹ ਕਿਵੇਂ ਕੰਮ ਕਰਦਾ ਹੈ:

- ਮਾਸਕ ਵਿੱਚ ਬਲੱਡ ਆਕਸੀਜਨ, ਦਿਲ ਦੀ ਗਤੀ, ਤਾਪਮਾਨ ਅਤੇ ਸਾਹ ਦੇ ਦਬਾਅ ਦਾ ਪਤਾ ਲਗਾਉਣ ਲਈ ਬਿਲਟ-ਇਨ ਸੈਂਸਰ ਹਨ ਜੋ ਤੁਹਾਡੇ ਮੌਜੂਦਾ ਮਹੱਤਵਪੂਰਨ ਡੇਟਾ ਨੂੰ ਲੈਂਦੇ ਹਨ ਅਤੇ ਪ੍ਰਕਿਰਿਆ ਕਰਦੇ ਹਨ

- ਡੇਟਾ ਨੂੰ ਛੋਟੀ ਸਕ੍ਰੀਨ 'ਤੇ ਦੇਖਿਆ ਜਾ ਸਕਦਾ ਹੈ ਜਦੋਂ ਕਿ ਇੱਕ ਵੈਬਸਾਈਟ 'ਤੇ ਵੀ ਭੇਜਿਆ ਜਾ ਸਕਦਾ ਹੈ ਜਿੱਥੇ ਇੱਕ ਮੈਡੀਕਲ ਪੇਸ਼ੇਵਰ ਤੁਹਾਡੇ ਮਹੱਤਵਪੂਰਨ ਡੇਟਾ ਦੀ ਨਿਗਰਾਨੀ ਕਰ ਸਕਦਾ ਹੈ ਅਤੇ ਇੱਕ ਨਿਦਾਨ ਜਾਂ ਇਲਾਜ ਦੇ ਸਕਦਾ ਹੈ।

- ਵੈਂਟੀਲੇਟਰ ਵਿੱਚ ਦੋ ਗਿਆਨ ਹਨ ਜੋ ਆਰਾਮਦਾਇਕ ਸਾਹ ਲੈਣ ਦੀ ਆਗਿਆ ਦੇਣ ਲਈ ਰੈਸਪੀਰੇਟਰ ਦੀ ਆਵਾਜ਼ ਅਤੇ ਗਤੀ ਦੇ ਸਮਾਯੋਜਨ ਦੀ ਆਗਿਆ ਦਿੰਦੇ ਹਨ।

ਕਦਮ:

1. ਡਿਵਾਈਸ ਨੂੰ ਇਸਦੀ ਪੈਕੇਜਿੰਗ ਤੋਂ ਧਿਆਨ ਨਾਲ ਖੋਲ੍ਹੋ

2. ਮਾਸਕ ਨੂੰ ਆਪਣੇ ਚਿਹਰੇ 'ਤੇ ਰੱਖੋ ਤਾਂ ਜੋ ਸਾਰੇ ਸੈਂਸਰ ਤੁਹਾਡੀ ਚਮੜੀ ਨਾਲ ਸੰਪਰਕ ਕਰ ਸਕਣ

3. ਹਰੇ ਬਟਨ ਦੀ ਵਰਤੋਂ ਕਰਕੇ ਡਿਵਾਈਸ ਨੂੰ ਚਾਲੂ ਕਰੋ

4. ਇੱਕ ਮਿੰਟ ਉਡੀਕ ਕਰੋ ਅਤੇ ਫਿਰ ਇਹ ਯਕੀਨੀ ਬਣਾਉਣ ਲਈ LCD ਦੀ ਜਾਂਚ ਕਰੋ ਕਿ ਸਿਹਤ ਡੇਟਾ ਲਿਆ ਜਾ ਰਿਹਾ ਹੈ

5. ਆਦਰਸ਼ ਆਰਾਮ ਲਈ ਨੌਬਸ ਦੀ ਵਰਤੋਂ ਕਰਕੇ ਵੈਂਟੀਲੇਟਰ ਸੈਟਿੰਗ ਨੂੰ ਐਡਜਸਟ ਕਰੋ।

Gujrati

સ્માર્ટ પોર્ટેબલ વાઇટલ મોનિટરિંગ રેસ્પિરેટર કેવી રીતે ચલાવવું

તે કેવી રીતે કાર્ય કરે છે:

- માસ્કમાં બ્લડ ઓક્સિજન, હૃદયના ધબકારા, તાપમાન અને શ્વસન દબાણ શોધવા માટે બિલ્ટ-ઇન સેન્સર છે જે તમારા વર્તમાન મહત્વપૂર્ણ ડેટાને લે છે અને પ્રક્રિયા કરે છે.

- ડેટા નાની સ્ક્રીન પર જોઈ શકાય છે અને સાથે સાથે વેબસાઇટ પર પણ મોકલી શકાય છે જ્યાં તબીબી વ્યાવસાયિક તમારા મહત્વપૂર્ણ કાર્યોનું નિરીક્ષણ કરી શકે છે અને નિદાન અથવા સારવાર આપી શકે છે.

- વેન્ટિલેટરમાં બે નો છે જે આરામદાયક શ્વાસ લેવા માટે વોલ્યુમ અને રેસ્પિરેટરની ગતિને સમાયોજિત કરવાની મંજૂરી આપે છે.

પગલાં:

1. ઉપકરણને તેના પેકેજિંગમાંથી કાળજીપૂર્વક અનબોક્સ કરો

2. માસ્કને તમારા ચહેરા પર મૂકો જેથી બધા સેન્સર તમારી ત્વચાને સ્પર્શ કરે.

3. લીલા બટનનો ઉપયોગ કરીને ઉપકરણને ચાલુ કરો.

4. એક મિનિટ રાહ જુઓ અને પછી આરોગ્ય ડેટા લેવામાં આવી રહ્યો છે તેની ખાતરી કરવા માટે LCD તપાસો.

5. આદર્શ આરામ માટે નોબ્સનો ઉપયોગ કરીને વેન્ટિલેટર સેટિંગને સમાયોજિત કરો.

Hindi

स्मार्ट पोर्टेबल वाइटल मॉनिटरिंग रेस्पिरेटर को कैसे संचालित करें

यह कैसे काम करता है:

- मास्क में रक्त ऑक्सीजन, हृदय गति, तापमान और श्वसन दबाव का पता लगाने के लिए अंतर्निर्मित सेंसर लगे हैं, जो आपके वर्तमान महत्वपूर्ण डेटा को लेते और संसाधित करते हैं।

- डेटा को छोटी स्क्रीन पर देखा जा सकता है और साथ ही इसे एक वेबसाइट पर भी भेजा जाता है, जहां एक चिकित्सा पेशेवर आपके महत्वपूर्ण डेटा की निगरानी कर सकता है और निदान या उपचार प्रदान कर सकता है।

- वेंटिलेटर में दो नॉब हैं जिनकी मदद से सांस लेने की गति और मात्रा को समायोजित किया जा सकता है, जिससे आरामदायक सांस लेना संभव हो सके।

चरण:

1. डिवाइस को उसकी पैकेजिंग से सावधानीपूर्वक निकालें।

2. मास्क को अपने चेहरे पर इस तरह लगाएं कि सभी सेंसर आपकी त्वचा के संपर्क में हों।

3. हरे बटन का उपयोग करके डिवाइस को पहनें।

4. एक मिनट प्रतीक्षा करें और फिर एलसीडी स्क्रीन पर यह सुनिश्चित करें कि स्वास्थ्य डेटा लिया जा रहा है।

5. आदर्श आराम के लिए नॉब का उपयोग करके वेंटिलेटर की सेटिंग को समायोजित करें।

Tamil/Malayalam

ஸ்மார்ட் போர்ட்டபிள் வைட்டல் கண்காணிப்பு சுவாசக் கருவியை எவ்வாறு இயக்குவது

இது எவ்வாறு செயல்படுகிறது:

- இரத்த ஆக்ஸிஜன், இதயத் துடிப்பு, வெப்பநிலை மற்றும் சுவாச அழுத்தத்தைக் கண்டறிய முகமூடியில் தற்போதைய முக்கிய தரவை எடுத்து செயலாக்குகின்றன

- தரவை சிறிய திரையில் பார்க்க முடியும், அதே நேரத்தில் ஒரு மருத்துவ நிபுணர் உங்கள் முக்கியத்துவத்தைக் கண்காணித்து

- சுவாசக் கருவியின் அளவையும் வேகத்தையும் சரிசெய்ய அனுமதிக்கும் இரண்டு சாதனங்கள் வென்டிலேட்டரில் உள்ளன, அவை வசதியான சுவாசத்தை அனுமதிக்கின்றன.

படிகள்:

1. சாதனத்தை அதன் பேக்கேஜிங்கிலிருந்து கவனமாக அவிழ்த்து விடுங்கள்

2. அனைத்து சென்சார்களும் உங்கள் தோலைத் தொடர்பு கொள்ளும் வகையில் முகமூடியை உங்கள் முகத்தில்

3. பச்சை பொத்தானைப் பயன்படுத்தி சாதனத்தை இயக்கவும்

4. ஒரு நிமிடம் காத்திருந்து, பின்னர் சுகாதாரத் தரவு எடுக்கப்படுவதை உறுதிசெய்ய LCD ஐச் சரிபார்க்கவும்

5. சிறந்த வசதிக்காக கைப்பிடிகளைப் பயன்படுத்தி வென்டிலேட்டர் அமைப்பை சரிசெய்யவும்.

Sinhala

ස්මාර්ට් අතේ ගෙන යා හැකි අත්‍යවශ්‍ය අධීක්ෂණ ශ්වසන යන්ත්‍රය ක්‍රියාත්මක කරන්නේ කෙසේද?

එය ක්‍රියා කරන ආකාරය:

- රුධිර ඔක්සිජන්, හෘද ස්පන්දන වේගය, උෂ්ණත්වය සහ ශ්වසන පීඩනය හඳුනා ගැනීම සඳහා ආවරණයේ සංවේදක සවි කර ඇති අතර එමඟින් ඔබේ වත්මන් වැදගත් දත්ත ලබාගෙන සකසනු ලැබේ

- දත්ත කුඩා තිරය මත නැරඹිය හැකි අතර වෛද්‍ය වෘත්තිකයෙකුට ඔබේ වැදගත් දත්ත නිරීක්ෂණය කර රෝග විනිශ්චය හෝ ප්‍රතිකාර ලබා දිය හැකි වෙබ් අඩවියකට ද යැවිය හැකිය.

- සුවපහසු හුස්ම ගැනීම සඳහා ශ්වසන යන්ත්‍රයේ පරිමාව සහ වේගය සකස් කිරීමට ඉඩ සලසන දැනුම්දීම් දෙකක් වාතාශ්‍රක යන්ත්‍රයට ඇත.

පියවර:

1. උපාංගය එහි ඇසුරුම්කරණයෙන් ප්‍රවේශමෙන් ඉවත් කරන්න

2. සියලුම සංවේදක ඔබේ සමට සම්බන්ධ වන පරිදි වෙස් මුහුණ ඔබේ මුහුණ මත තබන්න

3. හරිත බොත්තම භාවිතයෙන් උපාංගය ක්‍රියාත්මක කරන්න

4. මිනිත්තුවක් රැඳී සිට සෞඛ්‍ය දත්ත ලබා ගන්නා බව සහතික කර ගැනීමට LCD පරීක්ෂා කරන්න

5. පරිපූර්ණ සුවපහසුව සඳහා බොත්තම් භාවිතයෙන් වාතාශ්‍රක සැකසුම සකසන්න.

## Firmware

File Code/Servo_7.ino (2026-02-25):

// Servo_W.ino
// Potentiometer + Motor
/*

// Config ---------------------------------------------------------------------------
#include <Arduino.h>
#include <Servo.h>
#include <math.h>


// Private State ---------------------------------------------------------------------------
static Servo myServo;
// Internal pin storage for the file
static int _oscServoPin;
static int _oscSpeedPot;
static int _oscSwingPot;
// Sets the oscillation state
static int   direction = 1;
static float position  = 90.0f;
// Sets the time
static unsigned long lastMoveTime = 0;
// Smooths the pot values
static float speedSmooth = 0.0f;
static float swingSmooth = 0.0f;


// Public State ---------------------------------------------------------------------------
void ServoOsc_begin(int servoPin, int speedPotPin, int swingPotPin) {

  // Sets internal pins
  _oscServoPin = servoPin;
  _oscSpeedPot = speedPotPin;
  _oscSwingPot = swingPotPin;

  // Maps RP2040 
  analogReadResolution(12);       
  myServo.attach(_oscServoPin);
  myServo.write(90);

  // Initialise smoothing so it doesn't crawl at startup
  // Initialises smotthing to stop crawl at the start
  speedSmooth = analogRead(_oscSpeedPot);
  swingSmooth = analogRead(_oscSwingPot);

  // Sets fixed constants
  position = 90.0f;
  direction = 1;
  lastMoveTime = millis();
}

void ServoOsc_update() {
  unsigned long now = millis();

  // SPEED POT --------------------------------------------
  int speedRaw = analogRead(_oscSpeedPot);
  speedSmooth = 0.90f * speedSmooth + 0.10f * speedRaw;

  float x = speedSmooth / 4095.0f;
  float curved = powf(x, 2.4f);

  const int minMs = 2;
  const int maxMs = 20;
  int stepInterval = minMs + (maxMs - minMs) * curved;
  stepInterval = constrain(stepInterval, minMs, maxMs);


  // SWING POT --------------------------------------------
  int swingRaw = analogRead(_oscSwingPot);
  swingSmooth = 0.90f * swingSmooth + 0.10f * swingRaw;

  float amplitude = map((int)swingSmooth, 0, 4095, 20, 2);
  amplitude = constrain(amplitude, 0, 90);

  float minAngle = 90.0f - amplitude;
  float maxAngle = 90.0f + amplitude;


  // SERVO UPDATE --------------------------------------------
  if (now - lastMoveTime >= (unsigned long)stepInterval) {
    lastMoveTime = now;

    if (amplitude < 0.5f) {
      position = 90.0f;
      direction = 1;
    } else {
      position += direction * 2.5f;

      if (position >= maxAngle) { position = maxAngle; direction = -1; }
      if (position <= minAngle) { position = minAngle; direction =  1; }
    }

    // Sets servo state
    myServo.write((int)position);
  }

  static uint32_t dbg = 0;
  if (millis() - dbg > 300) {
    dbg = millis();
    Serial.print("speedRaw="); Serial.print(speedRaw);
    Serial.print(" swingRaw="); Serial.print(swingRaw);
    //Serial.print(" intervalMs="); Serial.print(intervalMs);
    Serial.print(" pos="); Serial.print(position);
    Serial.print(" amp="); Serial.println(amplitude);
  }

}
*/

#include <Arduino.h>
#include <Servo.h>
#include <math.h>

// ---------------- Pins ----------------
static int g_servoPin;
static int g_speedPotPin;
static int g_swingPotPin;


// ---------------- Tuning ----------------
static const int SERVO_ADC_MIN = 40;
static const int SERVO_ADC_MAX = 4050;

static const float EMA_ALPHA = 0.18f;
static const uint32_t SERVO_WRITE_PERIOD_MS = 20;

static const float SWING_MAX_DEG = 90.0f;
static const float SPEED_MIN_DPS = 20.0f;
static const float SPEED_MAX_DPS = 260.0f;

static const float AMP_SLEW_DPS  = 600.0f;
static const float SPD_SLEW_DPS2 = 2500.0f;

// ---------------- State ----------------
static Servo servo;

static float speedFilt = 0.0f;
static float swingFilt = 0.0f;

static float ampDeg = 0.0f;
static float spdDps = 60.0f;

static float posDeg = 90.0f;
static float dir    = 1.0f;

static uint32_t lastMs = 0;
static uint32_t lastWriteMs = 0;
static int lastWrittenDeg = 90;

static bool ready = false;

// ---------------- Helpers ----------------
static float clampf(float x, float lo, float hi) {
  if (x < lo) return lo;
  if (x > hi) return hi;
  return x;
}

static float ema(float prev, float x) {
  return prev + EMA_ALPHA * (x - prev);
}

static int readAdcAvg(int pin, int n = 4) {
  long sum = 0;
  for (int i = 0; i < n; i++) sum += analogRead(pin);
  return (int)(sum / n);
}

static float adcTo01(float adc) {
  float x = (adc - (float)SERVO_ADC_MIN) / (float)(SERVO_ADC_MAX - SERVO_ADC_MIN);
  return clampf(x, 0.0f, 1.0f);
}

// ---------------- PUBLIC API ----------------
void Servo_begin(int servoPin, int speedPotPin, int swingPotPin) {
  g_servoPin     = servoPin;
  g_speedPotPin  = speedPotPin;
  g_swingPotPin  = swingPotPin;

  analogReadResolution(12);

  pinMode(SPEED_POT_PIN, INPUT);
  pinMode(SWING_POT_PIN, INPUT);

  servo.attach(SERVO_PIN);
  servo.write(90);

  speedFilt = (float)readAdcAvg(SPEED_POT_PIN, 16);
  swingFilt = (float)readAdcAvg(SWING_POT_PIN, 16);

  ampDeg = 0.0f;
  spdDps = 60.0f;
  posDeg = 90.0f;
  dir = 1.0f;

  lastMs = millis();
  lastWriteMs = lastMs;
  lastWrittenDeg = 90;

  ready = true;
}

void Servo_update() {
  if (!ready) return;

  uint32_t now = millis();
  uint32_t dtMs = now - lastMs;
  if (dtMs == 0) return;
  lastMs = now;
  float dt = dtMs / 1000.0f;

  // ---- read + filter pots ----
  int speedRaw = readAdcAvg(g_speedPotPin, 8);
  int swingRaw = readAdcAvg(g_swingPotPin, 8);

  speedFilt = ema(speedFilt, (float)speedRaw);
  swingFilt = ema(swingFilt, (float)swingRaw);

  float speed01 = adcTo01(speedFilt); // 0..1 linear
  float swing01 = adcTo01(swingFilt); // 0..1 linear

  // ---- LINEAR targets ----
  float targetMaxAngle = swing01 * 90.0f;                 // 0..90 (absolute)
  float targetSpeed    = 20.0f + speed01 * (260.0f-20.0f);// linear

  // deadband so it can sit still at 0 without twitch
  if (targetMaxAngle < 1.0f) targetMaxAngle = 0.0f;

  // ---- slew-limit max angle + speed for smoothness ----
  float maxAngleStep = AMP_SLEW_DPS * dt;   // reuse your AMP_SLEW_DPS
  float aErr = targetMaxAngle - ampDeg;     // ampDeg now means "maxAngle"
  if (aErr >  maxAngleStep) ampDeg += maxAngleStep;
  else if (aErr < -maxAngleStep) ampDeg -= maxAngleStep;
  else ampDeg = targetMaxAngle;

  float maxSpeedStep = SPD_SLEW_DPS2 * dt;
  float sErr = targetSpeed - spdDps;
  if (sErr >  maxSpeedStep) spdDps += maxSpeedStep;
  else if (sErr < -maxSpeedStep) spdDps -= maxSpeedStep;
  else spdDps = targetSpeed;

  // ---- sweep between 0 and ampDeg (0..90) ----
  float minA = 0.0f;
  float maxA = ampDeg;          // <= 90

  if (maxA <= 0.5f) {
    posDeg = 0.0f;
    dir = 1.0f;
  } else {
    posDeg += dir * spdDps * dt;

    if (posDeg > maxA) { posDeg = maxA; dir = -1.0f; }
    if (posDeg < minA) { posDeg = minA; dir =  1.0f; }
  }

  // hard clamp so it NEVER exceeds 90
  if (posDeg < 0) posDeg = 0;
  if (posDeg > 90) posDeg = 90;

  // ---- write at fixed 50Hz ----
  if (now - lastWriteMs >= SERVO_WRITE_PERIOD_MS) {
    lastWriteMs = now;
    int deg = (int)round(posDeg);

    // write every time (smooth), don’t gate on >=1deg
    servo.write(deg);
    lastWrittenDeg = deg;
  }
}

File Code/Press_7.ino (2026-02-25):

// Press_W.ino
// Pressure Sensor


/*
// Config ---------------------------------------------------------------------------
#include <Arduino.h>
#define PRESSURE_PIN 28   // GP28 (ADC2)

// ADC constants
static const float VREF    = 3.3f;
static const int   ADC_MAX = 4095;

// MPX5100DP transfer function constants
static const float VS      = 3.3f;   // set this to the sensor supply you are ACTUALLY using
static const float OFFSET  = 0.04f;  // 4% of VS at 0 kPa
static const float SLOPE   = 0.009f; // 0.9% of VS per kPa

void Pressure_begin() {
  // No beginning needed
}

bool Pressure_read(float &kpa) {
  int reading = analogRead(PRESSURE_PIN);
  float vout = (reading / (float)ADC_MAX) * VREF;

  // MPX5100DP: P = (Vout/Vs - 0.04) / 0.009
  float pressure_kpa = ((vout / VS) - OFFSET) / SLOPE;

  if (pressure_kpa < 0) pressure_kpa = 0;
  kpa = pressure_kpa;
  return true;
}
*/

// Press_W.ino - MPX5100DP (3.3V supply, tare-to-zero)
#include <Arduino.h>
#define PRESSURE_PIN A2   // GP28 (ADC2)

static const float VREF    = 3.3f;
static const int   ADC_MAX = 4095;

static const float VS     = 3.3f;   // your sensor supply
static const float SLOPE  = 0.009f; // MPX5100DP slope term

static const int   N_SAMPLES = 32;

static bool  zeroed = false;
static float v0 = 0.0f;  // baseline Vout at rest (measured)

void Pressure_begin() {
  // optional:
  // analogReadResolution(12);
}

static float readVoutAvg() {
  long sum = 0;
  for (int i = 0; i < N_SAMPLES; i++) {
    sum += analogRead(PRESSURE_PIN);
    delayMicroseconds(150);
  }
  float raw = sum / (float)N_SAMPLES;
  return (raw / (float)ADC_MAX) * VREF;
}

bool Pressure_read(float &kpa) {
  float vout = readVoutAvg();

  // Tare at startup: whatever "rest" voltage is becomes zero pressure
  if (!zeroed) {
    v0 = vout;
    zeroed = true;
  }

  // Convert *change* in voltage to kPa
  // From Vout = Vs*(0.009*P + 0.04)  => dV = Vs*0.009*dP  => dP = dV/(Vs*0.009)
  float dp_kpa = (vout - v0) / (VS * SLOPE);

  if (dp_kpa < 0) dp_kpa = 0;   // clamp after tare
  kpa = dp_kpa;
  return true;
}

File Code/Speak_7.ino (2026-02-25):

// Alarm_6.ino
// Buzzer + Web "interrupt" banner when readings exceed limits.
// Works as a subfile (tab) in Arduino IDE, called from FYP_6.ino.

#include <Arduino.h>

// ---------------- USER LIMITS (EDIT THESE) ----------------
// Heart rate (BPM)
static float HR_MIN   = 0;
static float HR_MAX   = 120;

// Blood oxygen (SpO2 %)
static float SPO2_MIN = 0;
static float SPO2_MAX = 100;

// Temperature (°C)
static float TEMP_MIN = 2.0;
static float TEMP_MAX = 30.0;

// Pressure (kPa)  (edit to match your sensor/meaning)
static float PRESS_MIN = 0.0;
static float PRESS_MAX = 110.0;

// ---------------- Buzzer settings ----------------
static int      g_alarmPin = 15;     // GP15 default
static uint16_t BEEP_FREQ_HZ = 2200; // audible tone for the amp/speaker
static uint16_t BEEP_ON_MS   = 140;
static uint16_t BEEP_OFF_MS  = 120;

// ---------------- Alarm state ----------------
static bool   g_alarmActive = false;
static String g_alarmText   = "";

// Beep pattern (non-blocking)
static bool     g_beepRunning = false;
static uint8_t  g_beepCount   = 0;     // number of beeps already completed
static bool     g_beepOn      = false; // currently sounding
static uint32_t g_beepT0      = 0;

// Minimal JSON string escaper (quotes + backslashes + newlines)
static String jsonEscape(const String &in) {
  String o;
  o.reserve(in.length() + 8);
  for (size_t i = 0; i < in.length(); i++) {
    char c = in[i];
    if (c == '\\') o += "\\\\";
    else if (c == '"') o += "\\\"";
    else if (c == '\n') o += "\\n";
    else if (c == '\r') { /* skip */ }
    else o += c;
  }
  return o;
}

static bool outOfRange(float v, float vMin, float vMax) {
  if (!isfinite(v)) return false;
  return (v < vMin) || (v > vMax);
}

static void startBeep3() {
  g_beepRunning = true;
  g_beepCount   = 0;
  g_beepOn      = false;
  g_beepT0      = 0;
}

// Called frequently; advances the beep state machine
static void updateBeep() {
  if (!g_beepRunning) return;

  const uint32_t now = millis();

  if (g_beepT0 == 0) {
    // Start immediately
    g_beepOn = true;
    g_beepT0 = now;
    tone(g_alarmPin, BEEP_FREQ_HZ);
    return;
  }

  if (g_beepOn) {
    if (now - g_beepT0 >= BEEP_ON_MS) {
      // turn off
      noTone(g_alarmPin);
      g_beepOn = false;
      g_beepT0 = now;
      g_beepCount++; // one beep completed
      if (g_beepCount >= 3) {
        g_beepRunning = false;
      }
    }
  } else {
    // off time
    if (now - g_beepT0 >= BEEP_OFF_MS) {
      if (!g_beepRunning) return;
      g_beepOn = true;
      g_beepT0 = now;
      tone(g_alarmPin, BEEP_FREQ_HZ);
    }
  }
}

// ---------------- Public API (called from main) ----------------
void Alarm_begin(int pinGP) {
  g_alarmPin = pinGP;
  pinMode(g_alarmPin, OUTPUT);
  digitalWrite(g_alarmPin, LOW);
  noTone(g_alarmPin);

  g_alarmActive = false;
  g_alarmText   = "";
  g_beepRunning = false;
}

// Optional: call from main if you want to set limits in code instead of editing above
void Alarm_setLimits(float hrMin, float hrMax,
                     float spo2Min, float spo2Max,
                     float tempMin, float tempMax,
                     float pressMin, float pressMax) {
  HR_MIN = hrMin; HR_MAX = hrMax;
  SPO2_MIN = spo2Min; SPO2_MAX = spo2Max;
  TEMP_MIN = tempMin; TEMP_MAX = tempMax;
  PRESS_MIN = pressMin; PRESS_MAX = pressMax;
}

// Evaluate readings + update buzzer + store message for the webpage.
void Alarm_update(float bpm, float spo2, float tempC, float kpa) {
  // Build alarm message(s)
  String msg = "";
  bool any = false;

  if (outOfRange(bpm, HR_MIN, HR_MAX)) {
    any = true;
    msg += "Heart Rate out of range (" + String((int)round(bpm)) + " BPM; limits " + String((int)HR_MIN) + "-" + String((int)HR_MAX) + ")";
  }
  if (outOfRange(spo2, SPO2_MIN, SPO2_MAX)) {
    if (any) msg += " | ";
    any = true;
    msg += "SpO2 out of range (" + String((int)round(spo2)) + "%; limits " + String((int)SPO2_MIN) + "-" + String((int)SPO2_MAX) + ")";
  }
  if (outOfRange(tempC, TEMP_MIN, TEMP_MAX)) {
    if (any) msg += " | ";
    any = true;
    msg += "Temperature out of range (" + String(tempC, 1) + "C; limits " + String(TEMP_MIN, 1) + "-" + String(TEMP_MAX, 1) + ")";
  }
  if (outOfRange(kpa, PRESS_MIN, PRESS_MAX)) {
    if (any) msg += " | ";
    any = true;
    msg += "Pressure out of range (" + String(kpa, 1) + " kPa; limits " + String(PRESS_MIN, 1) + "-" + String(PRESS_MAX, 1) + ")";
  }

  // Rising edge: start beeps once
  if (any && !g_alarmActive) {
    startBeep3();
  }

  g_alarmActive = any;
  g_alarmText   = any ? msg : "";

  updateBeep();
}

bool Alarm_active() {
  return g_alarmActive;
}

String Alarm_text() {
  return g_alarmText;
}

// Convenience for JSON
String Alarm_textJsonEscaped() {
  return jsonEscape(g_alarmText);
}

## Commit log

2026-03-13 Update and rename Servo_7.ino to Code/Servo_7.ino
2026-03-13 Rename Poster Data.xlsx to Documentation/Poster Data.xlsx
    [Poster Data.xlsx]
2026-03-13 Rename Y3 Gantt.xlsx to Documentation/Y3 Gantt.xlsx
    [Y3 Gantt.xlsx]
2026-03-13 Rename 3D Mock Up.stl to CAD_3D/3D Mock Up.stl
    [3D Mock Up.stl]
2026-03-13 Rename Corner Brackets.stl to CAD_3D/Corner Brackets.stl
    [Corner Brackets.stl]
2026-03-13 Rename Solar Stand.stl to CAD_3D/Solar Stand.stl
    [Solar Stand.stl]
2026-03-13 Rename Vent Arm.stl to CAD_3D/Vent Arm.stl
    [Vent Arm.stl]
2026-03-13 Rename Vent Stand.stl to CAD_3D/Vent Stand.stl
    [Vent Stand.stl]
2026-03-13 Rename SOLAR BOX.dxf to CAD_LaserCut/SOLAR BOX.dxf
    [SOLAR BOX.dxf]
2026-03-13 Update and rename solar plate.dxf to CAD_LaserCut/solar plate.dxf
    [solar plate.dxf]
2026-03-13 Update and rename PCB_1.kicad_sch to Schematics/Vent.kicad_sch
    [Vent.kicad_sch]
2026-03-13 Update and rename Solar.kicad_sch to Schematics/Solar.kicad_sch
    [Solar.kicad_sch]
2026-03-13 Rename Circuit Diagram.pptx to Schematics/Circuit Diagram.pptx
2026-03-15 Rename Documentation/Y3 Gantt.xlsx to Documentation/Updates/Y3 Gantt.xlsx
    [Y3 Gantt.xlsx]
2026-03-15 Rename Documentation/Poster Data.xlsx to Documentation/Bench/Poster Data.xlsx
    [Poster Data.xlsx]
